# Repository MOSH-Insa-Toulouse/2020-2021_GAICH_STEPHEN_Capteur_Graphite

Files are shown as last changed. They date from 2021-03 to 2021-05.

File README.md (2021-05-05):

# 2020-2021 : Capteur Graphite GAICH-STEPHEN 
2020-2021 : Projet réalisé dans le cadre de l'Unité de Formation "du capteur au banc de test" en 4ème année Génie Physique, à l'INSA de Toulouse. Au cours de ce projet, nous avons réalisé un capteur de déformation/ jauge de contrainte à base de graphite 3H à 3B. Afin de mesurer la résistance de ce type de crayon, nous avons crée un dispositif bas-coût et transportable qui fut proposé par nos enseignants. Nous avons réalisé et fabriqué un PCB shield, à l'aide du logiciel Kicad, contenant un amplificateur transimpédance (circuit analogique) , un module Bluetooth, un écran OLED et un encodeur rotatoire. Ce dernier est pluggé sur un microcontrôleur Arduino Uno programmé à l'aide du logiciel Arduino IDE et contrôlé par une application android APK bluetooth. 

*** 
  - [Livrables](#livrables)
  - [PCB Shield](#pcb-shield)
  - [Code Arduino Mesure](#code-arduino-mesure)
  - [Application android APK](#application-android-apk)
  - [Banc de test](#banc-de-test)
  - [Code Arduino du banc de test](#code-arduino-du-banc-de-test)
  - [Protocole de test du capteur et les résultats obtenus](#protocole-de-test-du-capteur-et-les-résultats-obtenus)
  - [Datasheet capteur graphite](#datasheet-capteur-graphite)
  - [Problèmes rencontrés et améliorations à réaliser](#problèmes-rencontrés-et-améliorations-à-réaliser) 

*** 
## Livrables  

- [x] PCB shield 
- [x] Code Arduino permettant la mesure de R et le contrôle des fonctionnalités BT, OLED... 
- [x] Application android APK réalisé avec MIT APP INVENTOR.
- [x] Protocole de mesure et le programme Arduino pour le banc de test
- [x] Datasheet du capteur de déformation/ jauge de contrainte 

## PCB Shield
Utilisation des outils présents dans le logiciel Kicad pour créer le PCB: 
[KiCad EDA - Schematic Capture & PCB Design Software](https://kicad-pcb.org/), version: 5.1.8 

Le PCB Shield est pluggé sur un microcontrôleur Arduino Uno. Un amplificateur transimpédance, un module BT, un écran OLED et un encodeur rotatoire sont présents. 

Librairies de composants:
* Capacitor THT
* Resistor THT 
* Arduino Uno

#### Composants créés : symboles & empreintes 

- *Capteur Graphique*

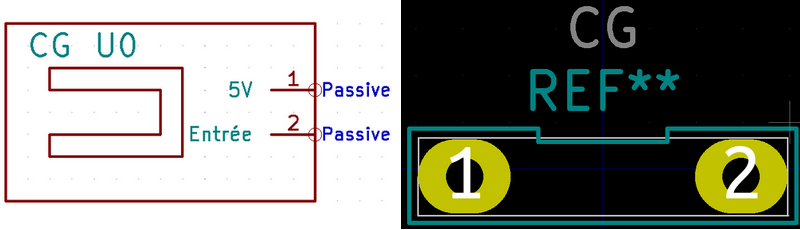
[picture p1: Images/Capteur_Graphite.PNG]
CG


- *Module Bluetooth*

BT

- *Encodeur rotatoire Keyes KY 040*

Encodeur

- *Ecran OLED*

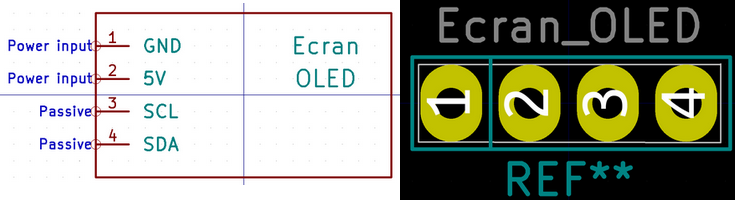
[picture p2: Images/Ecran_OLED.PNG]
Ecran


- *Amplificateur LT1050* (Empreinte déjà présente : DIP-8_W7.62mm_LongPads)

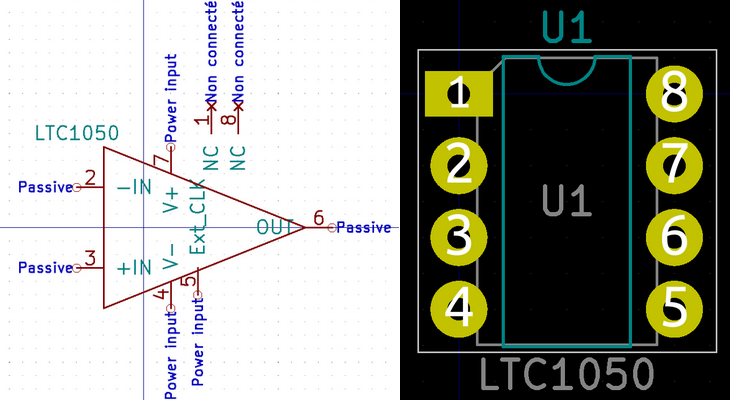
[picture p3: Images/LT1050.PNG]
LT1050


#### Schématique 

Dans le Eeschema, crée à partir d'un modèle Arduino Uno, nous avons regroupé les éléments suivant trois groupes : l'amplificateur transimpédance (circuit analogique qui permet de traiter les données envoyées par le capteur (variation de résistance)), les modules permettant d'ajouter des fonctionnalités au micro-contrôleur (module Bluetooth, encodeur rotatoire, écran OLED) et les broches de la carte Arduino Uno.  

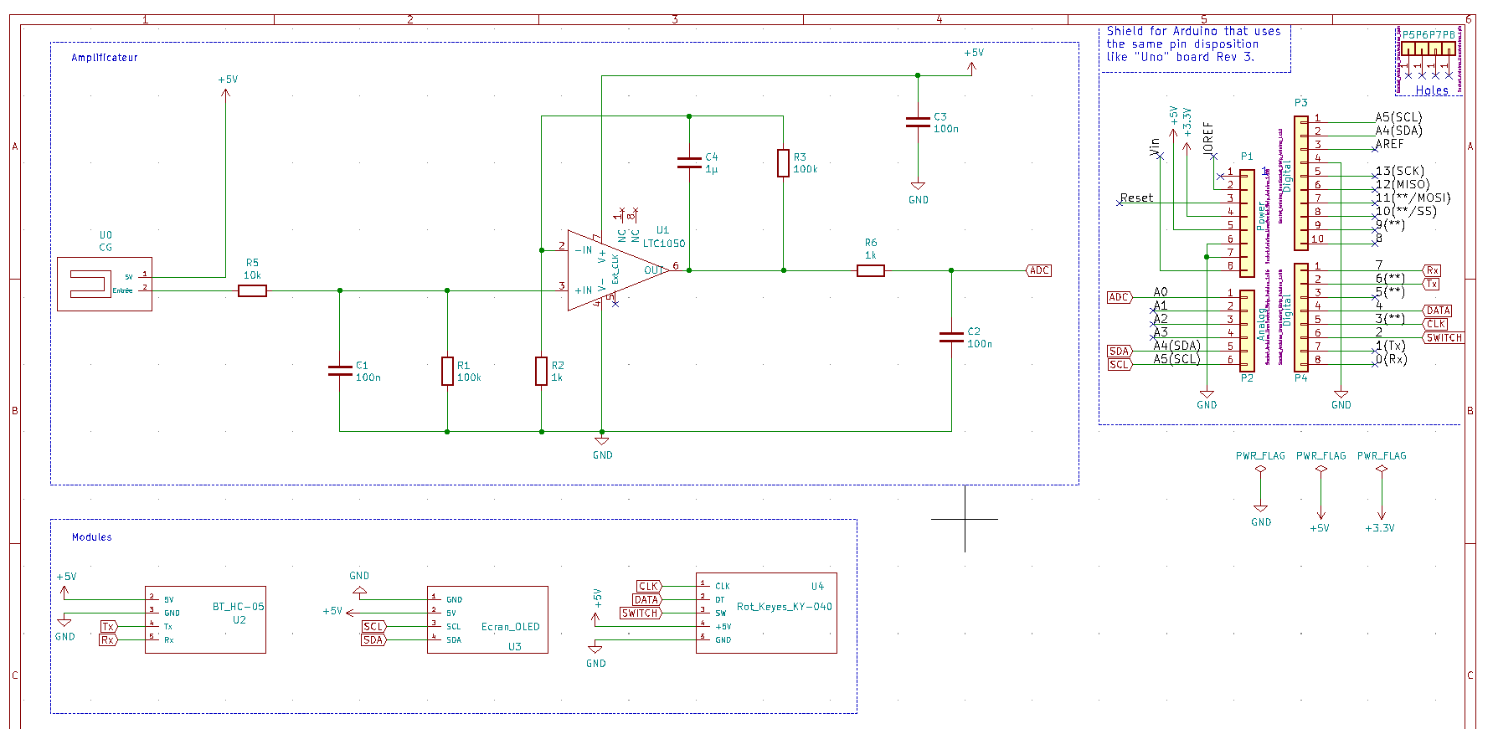
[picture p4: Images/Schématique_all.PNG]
Schematique


#### Placement des composants 

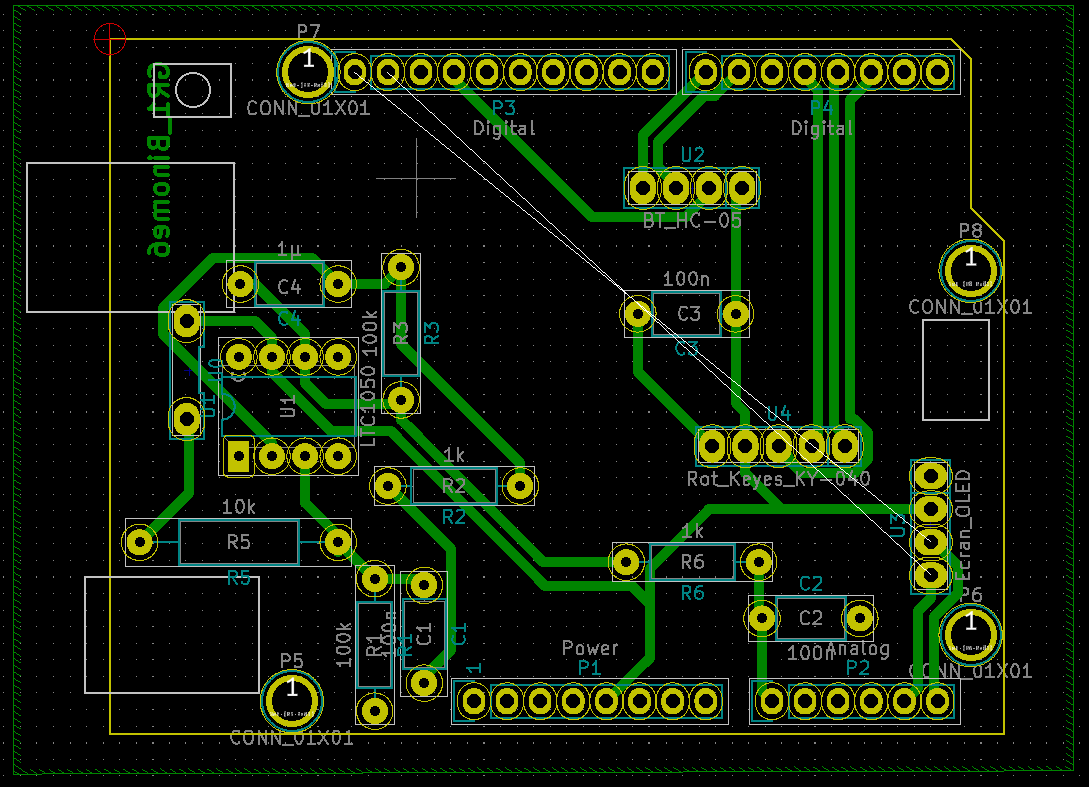
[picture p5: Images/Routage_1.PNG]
Placement


#### Routage 3D

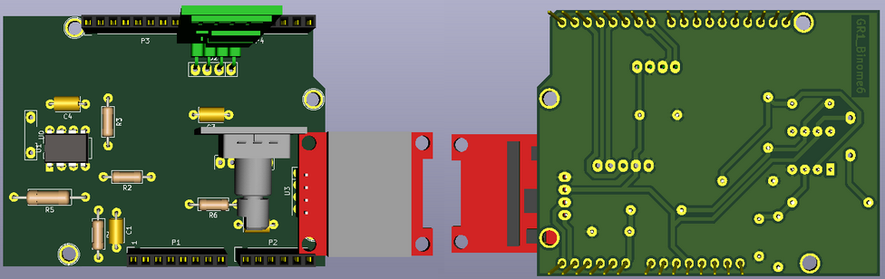
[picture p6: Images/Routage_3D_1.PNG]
Routage
 

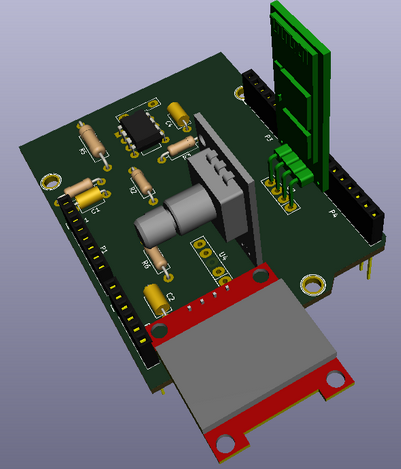
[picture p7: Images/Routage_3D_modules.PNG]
Routage


#### Soudage du PCB

Grâce à Catherine Crouzet, travaillant au Génie Physique, INSA Toulouse, nous avons pu réaliser notre PCB. Après avoir réalisé le schéma électrique, le placement des composants et le routage de la carte PCB sur le logiciel KiCad, le typon du PCB est imprimé sur deux feuilles calques. Les deux transparents sont alors superposés et scotchés entre eux afin de diminuer le risque de microcoupure (encre trop pale). Le typon est disposé sur la glace de l’insoleuse ainsi que la plaque d’époxy dont la face cuivrée (60µm) photosensible est "collée" au typon. Cette opération dure environ deux minutes et permet d’insoler la face photosensible. Le dessin du typon est alors visible sur la face cuivrée. La plaque est ensuite plongée dans un révélateur jusqu’à ce que le dessin apparaisse parfaitement (retire la résine non insolée). Après l’avoir rincé à l’eau, la plaque est alors prête pour la gravure. Le PCB est alors place dans un bain de perchlorure de fer rongeant tout le cuivre non protégé par la résine pendant sept minutes. Après l’avoir rincée à l’eau et vérifié le circuit, la résine est retirée avec de l’acétone. Le PCB sera ensuite percé et les composants seront soudés. 

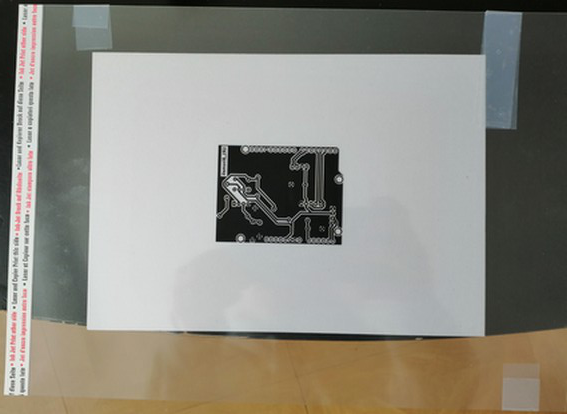
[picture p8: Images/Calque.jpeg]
Calque


Passons ensuite au perçage des trous de la plaquette à l'aide d'une perçeuse électrique [ici](Images/Perçeuse.jpg).
- 0.8mm pour ceux de l'AOP, des résistances et des capacités.
- 1mm pour ceux des connecteurs de l'Arduino et des headers des différents modules (pinces pour la feuille de graphite, bluetooth, encodeur rotatoire, écran OLED)

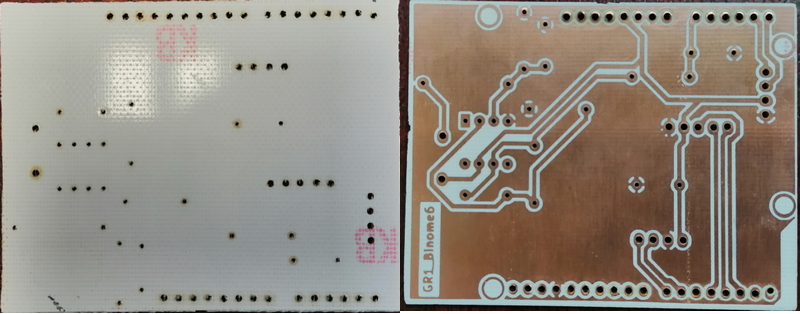
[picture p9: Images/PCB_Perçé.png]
Perçage


Pour finir, nous avons soudé chaque composant à l'aide d'un fer à souder. 

Remarque: il aurait fallu faire le diamètre des pads des connecteurs arduino plus gros afin d'avoir des soudures parfaites => peu de cuivre qui est resté autour après le perçage, ce qui a compliqué la soudure. 

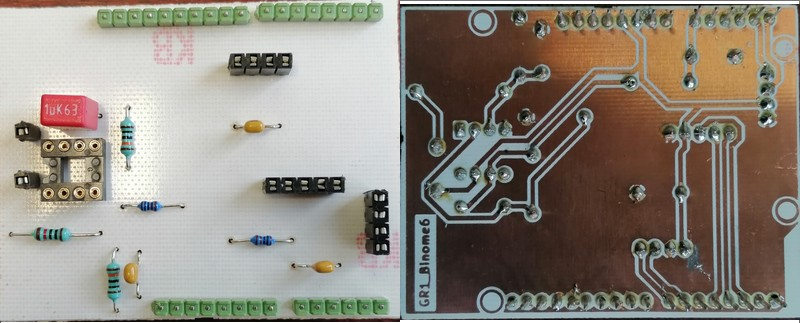
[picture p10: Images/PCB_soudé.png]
Soudure


#### Détail sur le conditionneur du capteur réalisé sur le shield (électronique analogique)
Nous avons détaillé cette partie dans la datasheet à la page 5 et 6 [ici](Datasheet/Datasheet_jauge_contrainte_GPINSA2021-2494-5215.pdf)

## Code Arduino Mesure 
Utilisation de l'environnement Arduino IDE téléchargeable [ici](https://www.arduino.cc/en/software); version 1.8.13.

Les librairies que nous avons utilisées sont disponibles [ici](PGM_Arduino_Mesure/Librairie).

Nous avons développé un programme permettant de mesurer la résistance de notre capteur. Vous pouvez le retrouver [ici](PGM_Arduino_Mesure/Programme_Capteur_Mesure/Programme_Capteur_Mesure.ino). 
Il s'agit d'un programme basique qui lira la valeur de la tension sur le pin A0 nommé comme "capteurgraphite". Cette acquisition est cadencée à 1s. La valeur lue est ensuite mappée sur 1 byte (0 à 255) car nous avons choisi d'envoyer un chiffre d'un byte sur le bluetooth. L'APK recevra un chiffre d'un byte à chaque tour de boucle. Cette valeur est également affichée sur le port série.

## Application android APK
Utilisation du site MIT App Inventor : [ici](https://appinventor.mit.edu/). 

Nous récupérons les données envoyées par le module bluetooth HC05 sur l'application et créons un fichier pour stocker ces dernières. 
Après de nombreux problèmes avec cet environnement et en s'inspirant du code crée par M.Grisolia, nous avons pu développer cette application. 

Face avant 

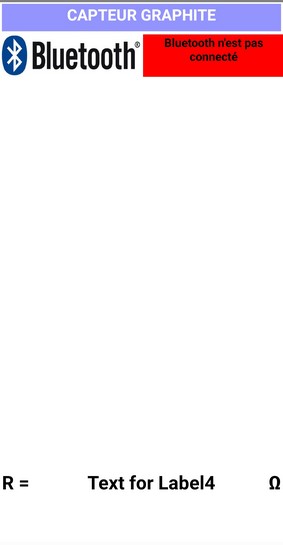
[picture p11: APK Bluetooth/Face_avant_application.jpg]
APKFaceAvant


Une connexion avec le bluetooth HC05 est nécessaire. Puis, vous pourrez suivre la variation de la tension lue par l'APK "en direct". La valeur de la résistance du capteur est aussi calculée et affichée en bas de l'écran. Enfin, un fichier contenant toutes les données récupérées par le bluetooth est créé dans vos documents. 

Vous trouverez le fichier .aia [ici](APK_Bluetooth/CAPTEUR_GRAPHITE_FILE.aia) et le fichier .apk [ici](APK_Bluetooth/CAPTEUR_GRAPHITE_FILE.apk)

Nous avons essayé d'améliorer cette version en faisant plusieurs screens. 
Une page d'accueil présente ci-dessous : 
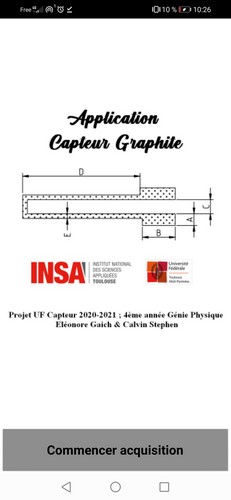
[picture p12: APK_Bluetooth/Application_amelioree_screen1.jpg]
page-accueil


Ensuite, sur la deuxième page après avoir cliqué sur le bouton "commencer l'acquisition", vous devez réaliser la mesure de la résistance initiale du capteur. Lorsque tous les voyants de l'étape 1 se mettent au vert, vous pouvez voir le tracé de la variation de la tension Vadc en fonction du temps au cours du temps. Les valeurs de la résistance du capteur et de la résistance relative sont aussi affichées.

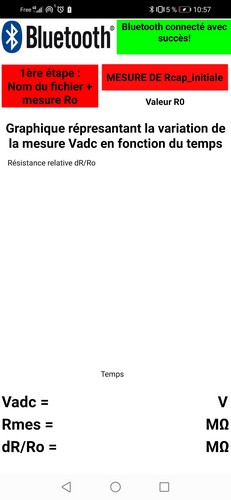
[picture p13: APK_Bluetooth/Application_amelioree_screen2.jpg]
Page-acquisition
 

Vous trouverez le fichier .aia [ici](APK_Bluetooth/Application_Capteur_amelioree.aia) et le fichier .apk [ici](APK_Bluetooth/Application_Capteur_amelioree.apk)

Plusieurs améliorations peuvent être réalisées. Nous les détaillerons dans la partie "Problèmes rencontrés et améliorations à réaliser".

## Banc de test 
Nous avons réalisé deux bancs de test "low-tech". Nous avons détaillé sa construction dans la datasheet afin que toute personne possédant notre capteur puisse retrouver les résultats que nous avons obtenus [ici](Datasheet/Datasheet_jauge_contrainte_GPINSA2021-2494-5215.pdf) à la page 7-8. De plus, étant réalisé à base de déchets ménagers, aucun matériel de haute technologie n'est nécessaire. 

Nous vous présentons nos deux bancs de test : 

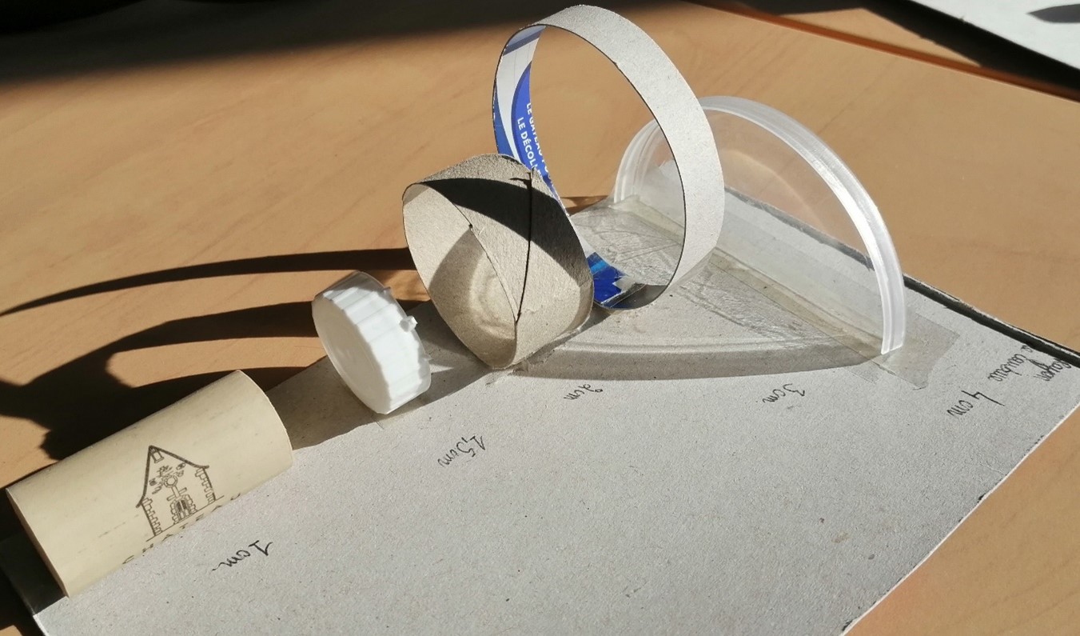
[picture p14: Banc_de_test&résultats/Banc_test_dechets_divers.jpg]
Banc_test_dechets


Figure : Banc de test « low-tech » n°1_ récupération de déchets divers

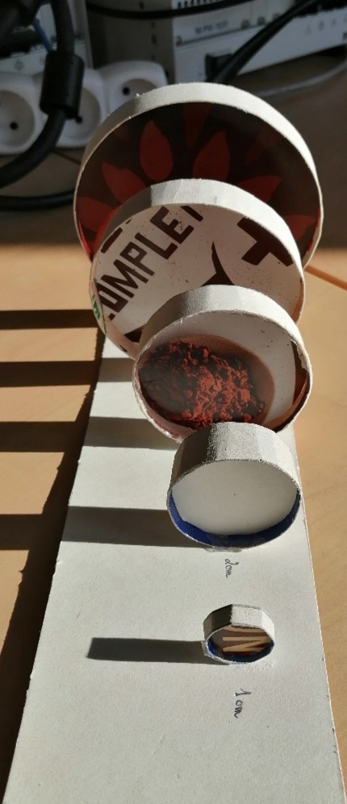
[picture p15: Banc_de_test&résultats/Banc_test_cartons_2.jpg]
Banc_test_carton


Figure : Banc de test « low-tech » n°2 _ carton

Au début, afin de diminuer les faux contacts entre les deux pinces crocodiles, nous avions utilisé un rouleau de papier toilette que nous avions troué (voir la photo ci-dessous).
Nous n'avons pas gardé cette méthode pour les mesures en tension et compression car les cercles créés sur le banc n'était pas à la même hauteur (amélioration possible).

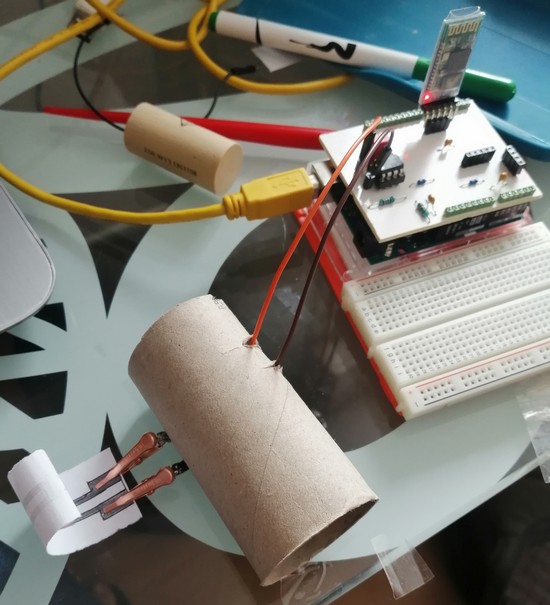
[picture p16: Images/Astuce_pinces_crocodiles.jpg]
Astucepince


## Code Arduino du banc de test 
Nous avons développé ce programme arduino afin de déterminer les valeurs obtenues en utilisant notre banc de test : [ici](PGM_Banc_de_test/PGM_Banc_de_test.ino).

Pour ce faire, nous avons du améliorer une librairie nous permettant de faire le "debouncing" sur l'encodeur rotatoire [ici](PGM_Arduino_Mesure/Librairie/Encoder_Polling_V2).

Notre nouveau programme gère aussi l'encodeur rotatoire et l'écran OLED. Ayant plusieurs banc de tests, nous avons programmé un menu sur l'écran OLED permettant à l'utilisateur de choisir le type de banc de test souhaité. Le boutton poussoir de l'encodeur rotatoire permet de selectionner ce dernier. Une fois le type de banc de test choisi, le programme envoie le type de banc de test à l'APK sous forme de "string" (texte). Dans le fichier des données enregistré sur le téléphone portable, chaque acquisition commence par des informations sur l'acquisition (banc de test, clock, forme des données reçues etc). Une fois cette étape terminée, l'OLED affiche la question "le bluetooth est- il connecté ?". L'utilisateur doit confirmer que la connexion a été établie en appuyant sur "Oui". Ensuite, il affiche "Etes-vous prêts ?" . L'utilisateur appuie de nouveau sur "Oui" une fois prêt. L'acquisition commence. La valeur de la tension Vadc est affichée sur l'OLED et est envoyée à l'APK via le bluetooth. Quand l'utilisateur souhaite arrêter l'acquistion, il doit appuyer sur le bouton 'STOP'. L'acquisition est alors arrêtée et l'OLED affiche de nouveau le menu principal.

## Protocole de test du capteur et les résultats obtenus 
Nous avons réalisé différentes expériences afin de déterminer les caractéristiques de notre capteur. 

#### Influence des dimensions du capteur 

Dans un premier temps, nous avons souhaité étudier l'influence des dimensions du capteur sur la résistance initiale. De ce fait, nous avons réalisé un plan d'expérience avec un modèle linéaire sans interactions de type TRI. Veuillez consulter ce document pour plus de détails sur la démarche : [ici](Banc_de_test&résultats/Banc_test_recherche_meilleur_capteur.docx) et sur les résultats obtenus [ici](Banc_de_test&résultats/Plan d'expérience_meilleures_dimensions.xlsx).

Nous avons pu identifier la réalité expérimentale (variables aléatoires de mesure) et tenter d’expliquer puis de maitriser au mieux les paramètres ayant un impact sur la résistance de notre capteur. Nous n’assurons pas que tous les paramètres influents furent identifiés. Elles ont aussi permis de vérifier que la résistance de notre capteur suivait la loi de Pouillet et donc la loi d’Ohm. Etant donné que nous ne sommes pas capables de déterminer le nombre de feuillets de graphite déposé lors du coloriage de notre capteur, nous allons étudier la variation relative en résistance ∆R/R_o = (R_mes-R_o)/R_o  afin d’homogénéiser nos mesures et pouvoir les comparer.  

#### Zone de non-déterioration du capteur

Dans un deuxième temps, nous nous avons essayé de determiner la zone de non-destruction du capteur. Après chaque mesure sur un rayon de courbure, nous avons noté la valeur de la tension du capteur au repos (non déformé) puis avons déterminé la résistance de ce dernier. Nous l’avons ensuite comparé à celle mesurée au début de la série de mesure. 
Document excel  [ici](Banc_de_test&résultats/Determination_zone_non_destruction_capteur.xlsx)

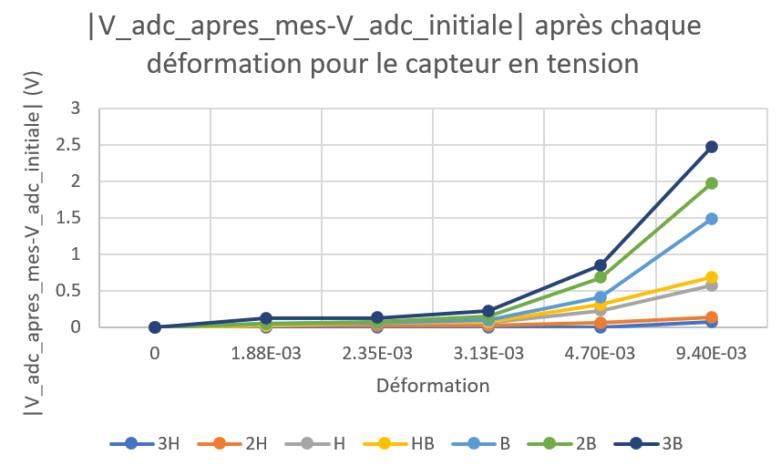
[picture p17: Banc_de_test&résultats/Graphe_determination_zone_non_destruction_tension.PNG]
Zone-non-destruction_tension


Figure : |Vadc_après_chaque_mesure - Vadc_initiale| après chaque déformation pour le capteur en tension

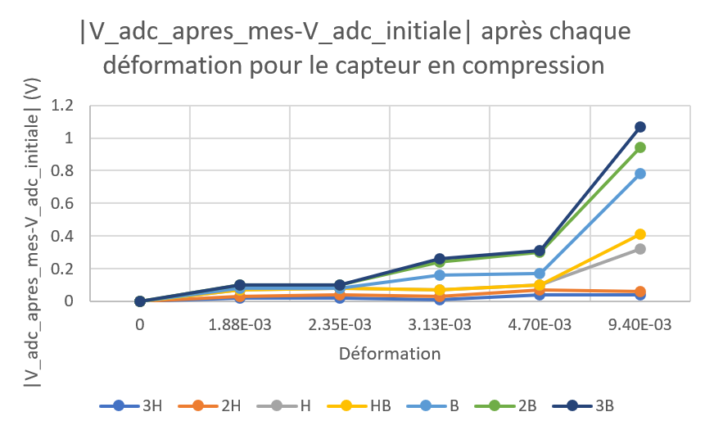
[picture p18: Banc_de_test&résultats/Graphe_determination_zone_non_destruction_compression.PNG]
Zone-non-destruction_tension


Figure : |Vadc_après_chaque_mesure - Vadc_initiale| après chaque déformation pour le capteur en compression

Voici notre conclusion : 

Zone-non-destruction

#### Influence du type de crayon utilisé pour colorier le capteur

Ensuite, nous avons étudie l'influence du type de crayon utilisé pour colorier notre capteur. Les crayons 3H, 2H, H, HB, B, 2B, et 3B furent testés successivement pour colorier notre capteur. Des tests de déformation, utilisant différents rayons de courbure de notre banc de test, sur ces capteurs furent réalisés. Ces informations sont présentes sur ces différents graphiques. Pour de détails, consultez le document excel [ici](Banc_de_test&résultats/Mesure_RayonCoubure_Crayons_Papiers.xlsx). 

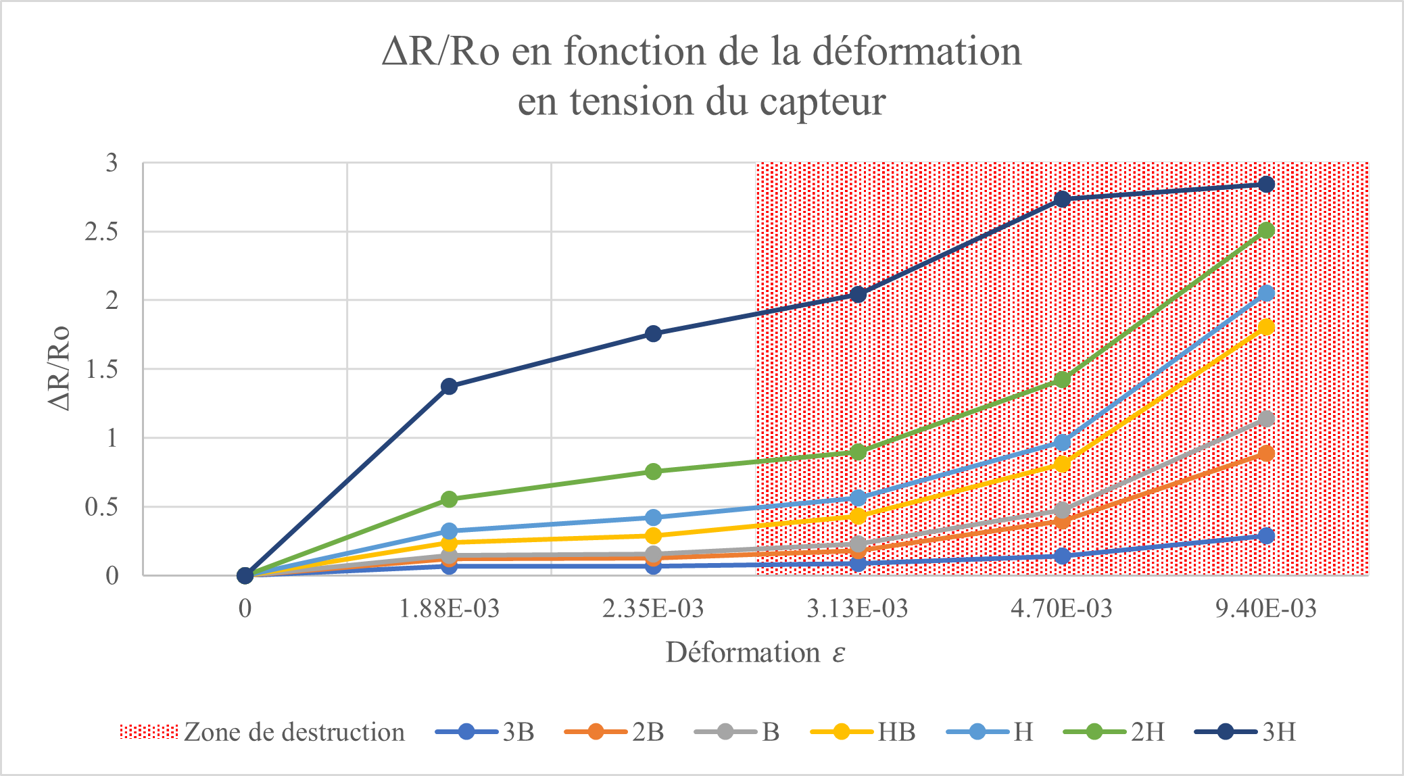
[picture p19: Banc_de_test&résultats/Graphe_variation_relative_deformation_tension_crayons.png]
Mesure_crayons_tension


Figure : Graphique représentant la variation relative de la résistance en fonction de la déformation en tension du capteur et du type de crayon présent sur le capteur

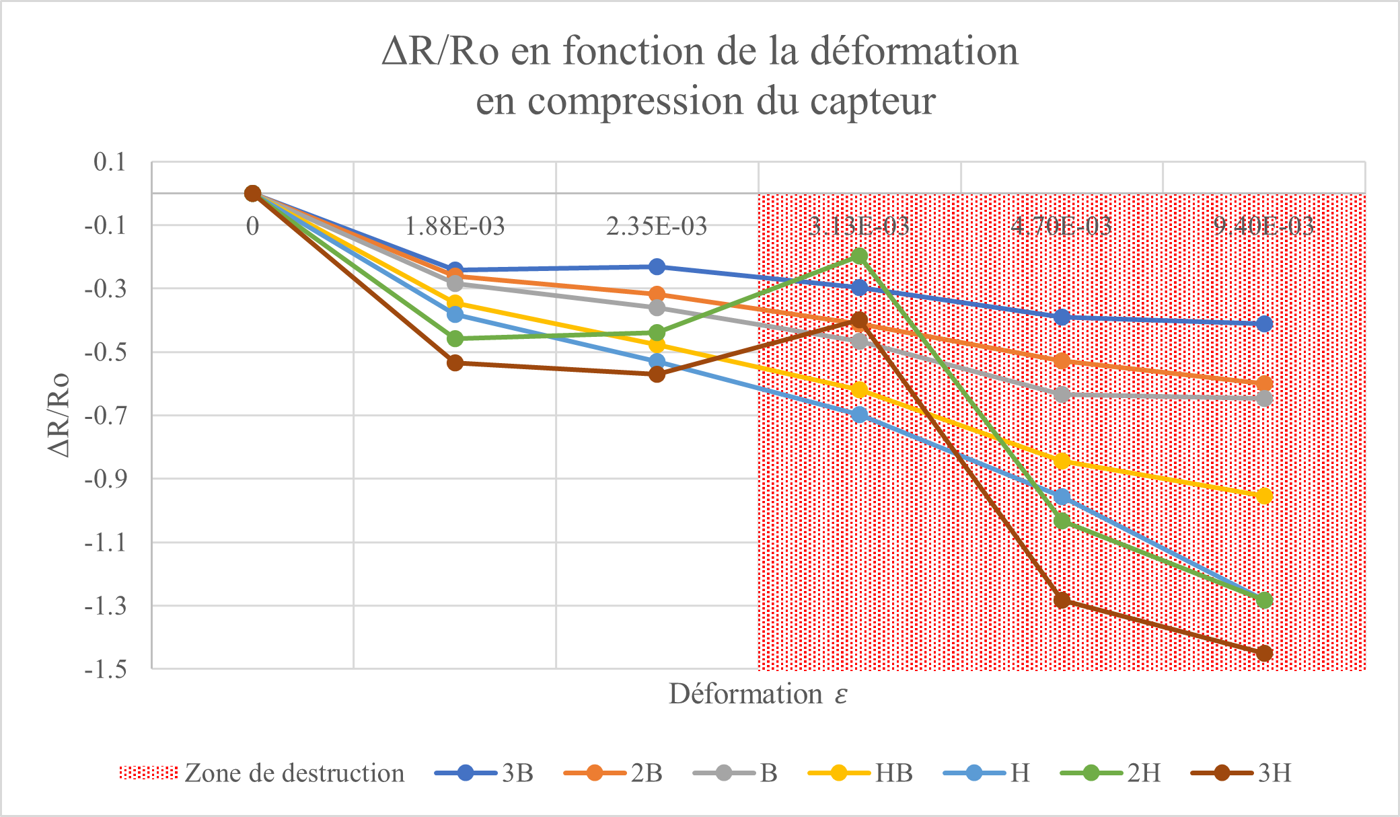
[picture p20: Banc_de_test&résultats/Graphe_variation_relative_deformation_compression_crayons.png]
Mesure_crayons_compression


Figure : Graphique représentant la variation relative de la résistance en fonction de la déformation en compression du capteur et du type de crayon présent sur le capteur

En conclusion de cette étude, le capteur colorié avec un crayon 3H est le plus sensible. En effet, pour ce capteur, la variation relative de la résistance ΔR/Ro est la plus grande. Cependant, en effectuant plusieurs expériences (colorier différents capteurs avec ce crayon), nous observons une large variabilité de la réponse. Lorsque le capteur est colorié avec des crayons 2H, H, HB, B, 2B et 3B, un comportement linéaire du ce dernier est observé. La sensibilité se définit comme le rapport entre sa valeur de sortie et sa valeur d'entrée. Lorsque le capteur est soumis à un mouvement de tension et de compression, la sensibilité du capteur augmente avec la dureté du crayon utilisé. En l’occurrence, le capteur colorié avec le crayon 3H est le plus sensible et celui colorié avec le crayon 3B est le moins sensible.

#### Influence du type de papier du capteur 

Enfin, nous avons étudié l'influence de type de papier. Nous avions émis l'hypothèse que la réponse du capteur serait différente en fonction du type de papier utilisé. Quand le capteur est réalisé sur du papier normal (70g/m²), la valeur de la résistance est trop faible pour être mesurée par notre conditionneur. La valeur de la tension Vadc est en saturation (5V). Une corrélation entre l’épaisseur du papier utilisé et la réponse du capteur existe. Nous avons détaillé une possible explication à ce phénomène dans la datasheet à la page 15. [ici](Datasheet/Datasheet_jauge_contrainte_GPINSA2021-2494-5215.pdf)

Pour pallier ce problème, le papier fut renforcé en enveloppant le capteur avec du ruban d’adhésif sans couvrir les pads du capteur pour la prise du contact avec les pinces crocodiles. Vous trouverez les résultats obtenus dans le fichier excel [ici](Banc_de_test&résultats/Influence_scotch.xlsx). En effectuant plusieurs tests sur le capteur, une tendance d'augmentation de la résistance est observée lorsque nous diminuons le rayon de courbure. Cependant, nous pouvons observer une augmentation initiale de la résistance entre un capteur scotché et un capteur sans ruban adhésif. Nous n’avons pas observé une amélioration de la zone de non-destruction. Dans certains cas, nous observons même une dégradation de cette dernière. Nous avons détaillé une possible explication à ce phénomène dans la datasheet à la page 15. [ici](Datasheet/Datasheet_jauge_contrainte_GPINSA2021-2494-5215.pdf)

## Datasheet capteur graphite
Vous pouvez retrouver la datasheet complète de notre capteur [ici](Datasheet/Datasheet_jauge_contrainte_GPINSA2021-2494-5215.pdf)

## Problèmes rencontrés et améliorations à réaliser

#### Problèmes sur le PCB

- Pads pour les connecteurs arduino trop fins.
- Mauvais placement de l'empreinte OLED : En testant l'écran OLED avec un programme fourni dans les libraires arduino, nous nous sommes rendus compte que, par inattention, nous avions mal placé l'empreinte (rotation 180°) car nous souhaitions que l'écran OLED soit positionné vers l'extérieur (cf PCB 3D). Afin d'avoir les bonnes pins, ce dernier doit être placé à l'intérieur. Or il y a l'encodeur rotatoire. Pour palier à ce problème, nous allons utiliser la platine d'expérimentation ou des fils males/femelle. 

  Améliorations : Nouveau PCB. 

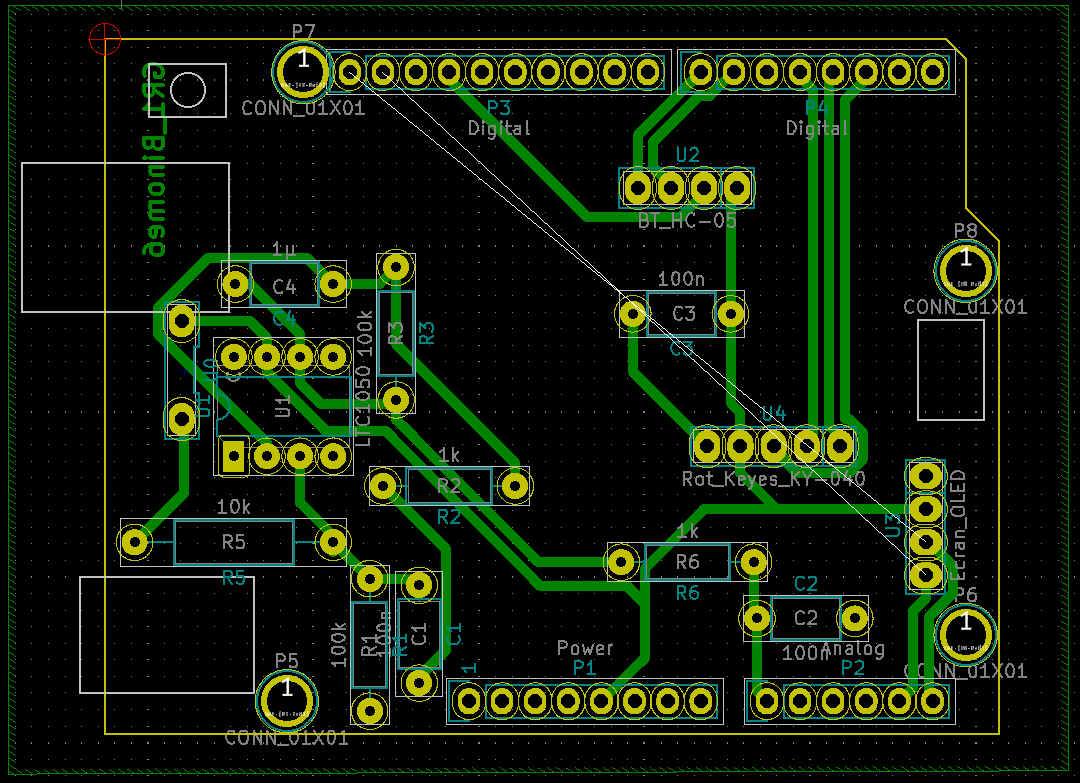
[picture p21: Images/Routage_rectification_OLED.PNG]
PCB_rectifié
  
  
#### Amélioration de l'application APK : Application capteur améliorée 
Après de multiples essais, nous n'avons pas réussi à afficher correctement la variation (dR-Ro)/Ro. Nous ne comprenons pas l'erreur commise. 
De plus, il faudrait optimiser le code pour que le traçage sur le canvas et les calculs de résistance se fassent en "temps réel". Nous avons un temps de décalage assez important. 
  
#### Améliorations sur la caractérisation du capteur 

Veuillez vous référer à notre datasheet présente [ici](Datasheet/Datasheet_jauge_contrainte_GPINSA2021-2494-5215.pdf) section Suggestions/Remarques. 

Nous avons détaillé différentes expérimentations que nous aurions aimées mener. Par manque de temps, nous n'avons pu les faire. 
De plus, afin de determiner concrètement les dimentions optimales du capteur, le plan d'expérience que nous avons mené devrait être complété par une étude plus approfondie (modèle de 2nd ordre) pour determiner l'optimum. Cependant, il faut pouvoir maitriser des paramètres qui ne sont pas contrôlables pour le moment (nombre de feuillets de graphite sur le capteur). 

***

## Note des auteurs 
Nous tenons à remercier Mme Crouzet, M.Grisolia et M.Biganzoli pour leur aide tout au long de ce projet ainsi que M.Constancias pour son aide lors de l'analyse des résultats obtenus sur notre DOE. 

Pour nous contacter : 
- Eléonore Gaich : gaich@etud.insa-toulouse.fr
- Calvin Stephen : stephen@etud.insa-toulouse.fr

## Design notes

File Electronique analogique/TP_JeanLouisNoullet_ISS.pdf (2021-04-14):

# ISS - UF Smart Devices : partie analogique

English version here

## 1. Mesure d'une résistance

Méthodes classiques :

- imposer I, mesurer V
- imposer V, mesurer I
- alimenter, mesurer V et I
- alimenter, mesurer R par identification (pont)

Cas du capteur de gaz à nano-particules :

- très faible courant : de l'ordre de 100 nA
- effet tunnel : forte non-linéarité de I(V)

Alors quelle technique adopter pour extraire l'information utile du capteur ?

## 2. Mesure de faible courant avec un micro-contrôleur

Parametres des microcontrôleurs courants en 2016
(AVR/Arduino, STM32, PIC Microchip, etc...) :
- résolution 10 à 12 bits (1024 à 4096 points)
- pleine échelle (VRef) de 1.1 V à 5.0 V
- impédance de source max 1 kOhm à 10 kOhm
- fréquence d'échantillonnage max 15 kHz à 2.4 MHz
La mesure directe d'un courant de 100 nA ne parait pas praticable.
N.B. la valeur max d'impédance de source est spécifiée en fonction de l' échantillonneur à capacité commutée présent à l'entrée de l'ADC.

Solution "classique" :

L'amplificateur transimpédance.

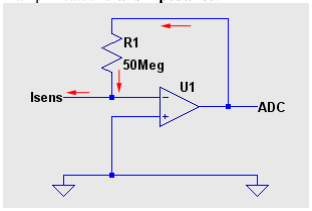
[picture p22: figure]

Problèmes posés par cette solution :

- nécessite une très grande valeur pour R1
- nécessite une tension négative pour alimenter le capteur

Solution "classique" améliorée :

L'amplificateur transimpédance suivi d'un étage amplificateur inverseur.

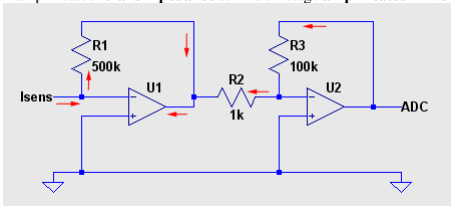
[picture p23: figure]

- grâce au gain du second étage, la résistance R1 n'a pas besoin d'être grande
- grâce à l'inversion, l'alimentation du capteur peut être positive
- cependant il faut une alimentation bipolaire pour les amplis

Solution minimaliste :

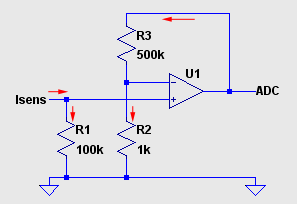
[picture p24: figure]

- conversion I-->U dans la résistance d'épreuve R1 (shunt)
- amplification à fort gain par montage non-inverseur
- la chute de tension sur R1 perturbe (un peu) la tension appliquée au capteur
- peut fonctionner avec seulement une alimentation positive

Remarques :
Gain de l’étage de l’AOP : (R2+R3)/R2=(1k+500k)/1k=501
Tension aux bornes de R1 : le courant Isens est d’environ 100nA
- V = 100kOhm*100nA=10⁻²V=10mV
Tension sur l’ADC : Gain*Tension aux bornes de R1 => 501*10x10⁻³~5V

Contraintes sur le choix de l'ampli :

- faible courant d'entrée

- ultra-faible offset de tension
- supporte mode commun à la tension d'alim négative ("low rail")

Remarques :
(1) offset voltage = erreur constante aux entrées de l’amplificateur différentiel dû à un état non compensé sur l’étage d’entrée de l’amplificateur. On veut que cet offset soit négligeable devant la tension mesurée sur R1 qui sera de 10mV.
(2) Le courant d’entrée doit être très petit devant Isens pour avoir le Isens traverse la R1 et pas l’entrée
(3) Mode commun : tension commune aux deux entrées, un bon amplifieur sera insensible à ce mode commun. Si le Isens =0A ,on veut 0V sur l’ADC. LTC1050C => 5µV offset voltage, et maximum offset voltage drift : 0.05µV/°C. Bien comparé aux 10mV aux bornes de R1.

L'ampli LTC1050C est disponible, satisfait-il ces contraintes ?

## 3. Filtrage passe-bas

Une bande passante de l'ordre de 1 Hz est largement suffisante pour extraire toute l'information utile du capteur, dont l'inertie est importante.

Un montage aussi sensible étant très vulnérable au bruit à 50Hz (+ harmoniques) résultant du couplage capacitif avec le réseau 230V, un filtrage passe-bas est indispensable.
D'autres sources de bruit à filtrer sont les horloges de circuits digitaux (microcontrôleur, afficheurs, etc...) et les transceivers RF (bluetooth, etc...).

Ce filtrage peut être effectué en partie du coté digital, par programme, sur le microcontrôleur.
Cependant un filtrage analogique est indispensable, en effet un excès de bruit à l'entrée de l'ADC pourrait amener celui-ci à saturation.
De plus un filtrage anti-repliement (anti-aliasing) est indispensable en raison de l'échantillonnage effectué par l'ADC.
Pour faciliter ce filtrage on a intérêt à faire fonctionner l'ADC à la plus GRANDE fréquence utilisable SANS PERTE DE QUALITE (dans le cas de l'Arduino Uno, 200kHz/13 = 15.4 kHz, avec un choix de prescaler à 128 ! (cf wiring.c).

Le filtrage peut s'implanter dans 3 régions de la chaîne de traitement analogique :

- filtre passif à l'entrée : permet d'éviter que les bruits HF causent de la distorsion dans les étages d'entrée
- filtre actif basé sur les amplificateurs opérationnels : maximum d'efficacité
- filtre passif en fin de chaine, coté ADC, pour retirer le bruit introduit en cours de traitement (bruit d'alimentation, bruit d'horloge des amplificateurs à découpage)

Schéma Suggéré

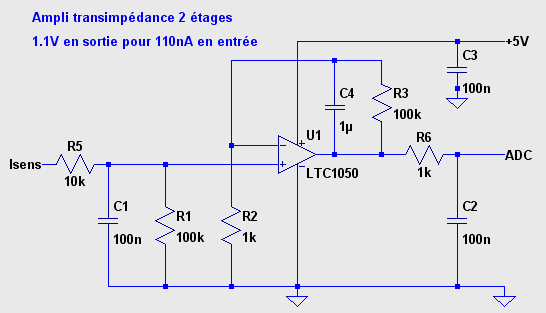
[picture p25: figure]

- R5 en entrée protège l'ampli opérationnel contre les décharges électrostatiques, en forme avec C1 un filtre pour les bruits en tension
- C1 avec R1 forme un filtre pour le bruit en courant
- R2 sera interchangeable, pour permettre une adaptation du calibre
- C4 avec R3 forme un filtre actif
- C2 avec R6 forme le filtre de sortie
- C3 filtre le bruit d'alimentation

## 4. Questions

A l’aide du simulateur LTSpice IV :

1. Vérifier la fonctionnalité dans les conditions nominales 2. L'incidence de l'offset de l'amplificateur LTC1050C est-elle acceptable ? 3. L'incidence du courant d'entrée de l'amplificateur est-elle acceptable ? 4. Quelle est la fréquence de coupure de chaque étage de filtre passe-bas ? 5. Quelle est l'atténuation globale d'un bruit en courant de 50 Hz ?

6. Quelle est l'atténuation globale d'un bruit en courant à la fréquence limite de repliement (dans le cas de l'ADC Arduino Uno) ?

### 7. Préparez une simulation de démonstration avec :

- un capteur alimenté en 5V dont la conductance varie de 10 nS à 20 nS en 0.5s (l’utilisation d’un filtre passe-bas pourrait être utile !).

### 1. Mettre en évidence l’intérêt du filtrage 50Hz choisi en visualisant

l’impact d’un bruit de 1% sur la source d’alimentation du capteur

### 2. Quand est-ce que ce bruit devient gênant ?

- Pour s’approcher des conditions réelles de mesures réalisées à l’AIME, vous modifierez le montage précédent pour mettre une alimentation de 20V sur le capteur (à la place de la 5V) et conserverez l’alimentation de 5V sur l’AOP.

### 1. Peut-on réaliser ce montage sur un Arduino Uno ?

- une source de bruit de 230V RMS à 50Hz, couplée au noeud d'entrée par une capacité de 1 pF
- Serait-il intéressant d’ajouter un montage dérivateur pour mesurer directement le coefficient cinétique de la réaction chimique du capteur avec un gaz ?

### 1. Si oui, proposez un montage !

N.B. pour simuler une conductance variable, utiliser l'élément Arbitrary current source (symbole BI) de LTSpice contrôlé par une source de tension indépendante représentant la variation de concentration du gaz atteignant le capteur

8. Donner une expression analytique de la résistance du capteur en fonction des éléments du circuit transimpédance.

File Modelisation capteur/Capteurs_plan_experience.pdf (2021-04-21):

Imprimé avec une version d'essai de
QCAD Professional

Merci d'essayer QCAD/CAM. Cette version d'essai vous permet d'essayer QCAD/CAM avant de

décider si vous voulez l'acheter. Il n'est pas destiné à un usage productif. Pour commencer à utiliser QCAD/CAM de façon productive, S'il

vous plaît achetez une version complète pour un prix modique auprès de notre boutique en ligne: qcad.org/shop. Avec votre achat, vous soutenez le développement futur de

QCAD. Merci!

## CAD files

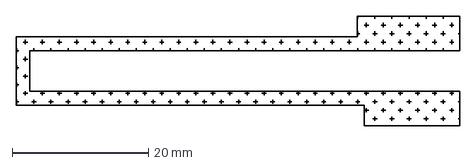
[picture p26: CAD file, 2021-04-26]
Modelisation capteur/Modelisation_capteur.dxf
65.0 x 16.0 mm

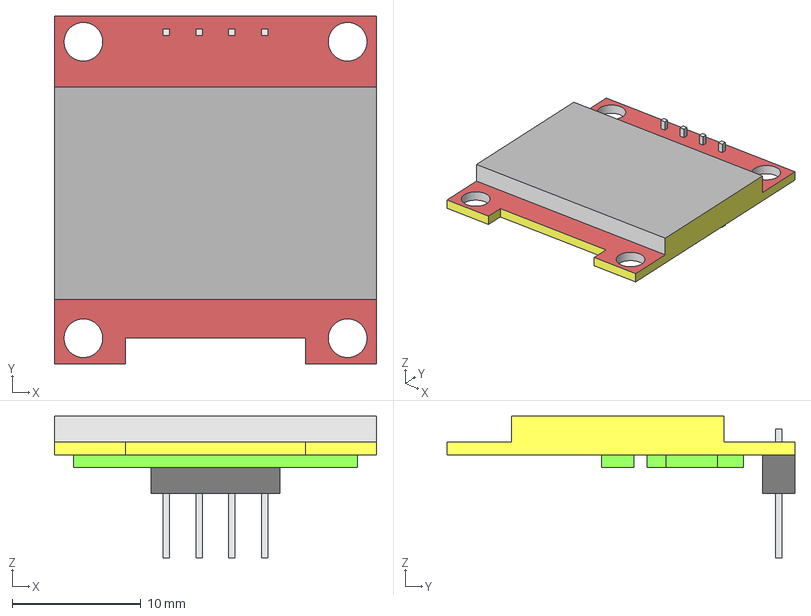
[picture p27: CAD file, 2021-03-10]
PCB_Shield/OLED_i2c_screen_3D.step
25.0 x 27.0 x 11.0 mm

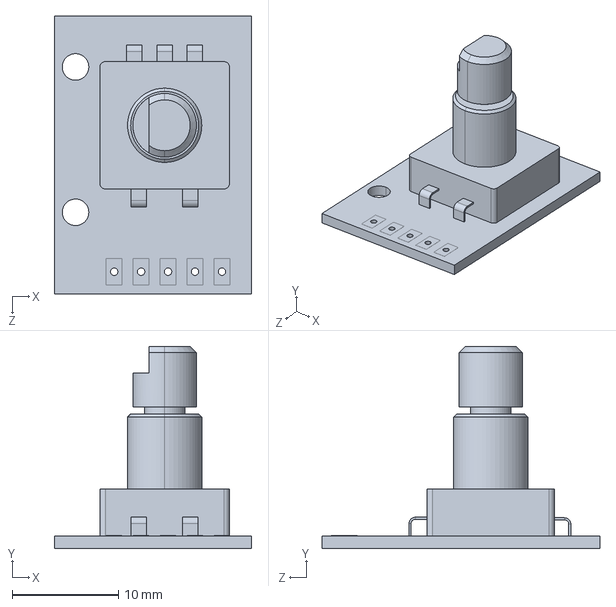
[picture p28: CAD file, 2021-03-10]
PCB_Shield/rotary-encoder-ky-040-1_3D/Encoder KY-040.STEP
18.6 x 19.1 x 26.2 mm

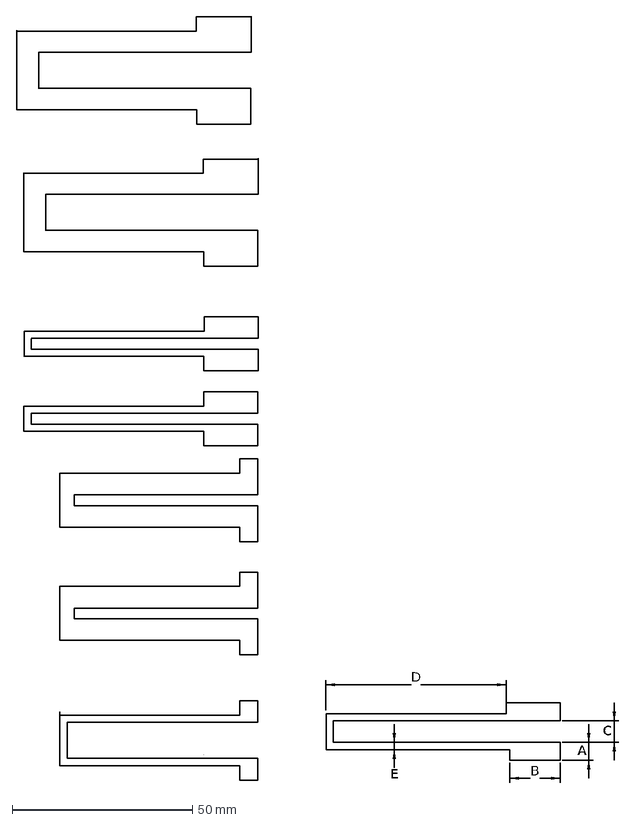
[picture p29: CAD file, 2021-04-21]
Modelisation capteur/#Capteurs_plan_experience.dxf
D
C
A
B
E

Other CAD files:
Modelisation capteur/Capteurs_plan_experience.dxf
PCB_Shield/rotary-encoder-ky-040-1_3D/Encoder KY-040.SLDPRT

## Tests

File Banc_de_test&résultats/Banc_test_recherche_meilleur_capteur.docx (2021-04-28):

RECHERCHE DU MEILLEUR CAPTEUR GRAPHITE

Déformation du capteur => coef de Poisson : déformation latérale et déformation longitudinale => comment le déterminer ? On néglige la déformation latérale ?

1ère étape : déterminer les dimensions idéales du capteur

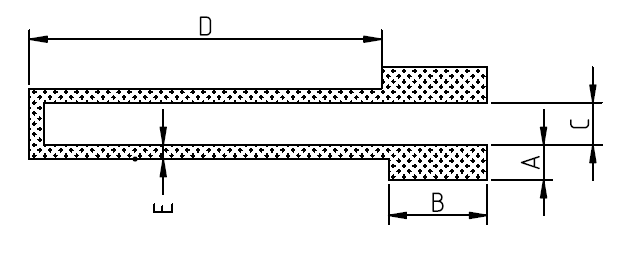
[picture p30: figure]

Légende :

A : largeur des pads [0.5 ; 1]cm

B : hauteur du pad [0.5 ; 1.5]cm

C : écartement des pads [0.3 ; 0.6]cm

D : longueur du capteur [1 ;5]cm

E : largeur du capteur [0.2 ;0.6]cm

Paramètre qu’on ne peut pas prendre en compte : nombre de feuilles de graphite déposé sur la feuille papier + le nombre de fibres papier qui sont rompus lors d’un essai

Détail plan d’expérience fichier excel

Faire un plan d’expérience avec modèle linéaire en prenant matrice Hadamard avec -1 : valeur min testée et 1 : valeur max en faisant une matrice normalisée

Chaque capteur sera testé sur un rayon de courbure du banc de test « low tech » :

- 1cm
- 2cm
- 3cm
- 4cm
- 5cm

Bilan :

1. Biais de mesure, id des paramètres expérimentaux que nous ne maitrisons pas => nombre de feuille de graphite déposé, coloriage régulier => INFLUENCE grandement la mesure (vu aussi avec les crayons graphite). Grande variabilité des résultats.
2. Vadc = 0 : pourquoi ? Seulement par le peu de graphite déposé ? Résultat d’une mesure en dehors de la sensibilité de l’ampli/ chaine d’instrumentation => Faire un étalonnage de la sensibilité de la mesure avec des résistances étalons et vérifier la précision (suggestions). Voir si certaines électrodes => pinces croco prennent de bonnes prises de contact pour quelque chose d’aussi faibles ? Un autre moyen de prendre le contact qui serait plus fiable et précis ? Ex : fourmi sur pèse personne => poids ?
3. Procédé de fabrication est très variable => propriétés du matériau déposées sont aussi variables. Feuillets de graphite déposés par coloriage => changement de la résistivité + points de contact qui influencent la résistance totale du capteur.
4. Comment s’assurer de la répétabilité de nos expériences : se fixer des conditions sur le coloriage ? Force, sens ? Conditions sur les prises de contact ? Où, comment ? => changement visible en fonction de l’endroit sur le pad différent : du au nombre de feuillets de graphite déposé mais aussi à un autre paramètre ? Pinces croco ayant une R trop importante ?
5. Définition de la résistance : résistivité qui dépend de la longueur + section de la conduction => ici vérifier avec les paramètres C,D,E + nombre de couches de graphite (vu au niveau des valeurs de R mesurées mais pas possible de le déterminer) => comment estimer l’epaisseur d’un trait de graphite => permettrait de remonter au nombre de feuillets de graphite déposées à l’origine de la conductivité : avec une balance de précision ? Assez précis ? http://wiki.scienceamusante.net/index.php/Estimer_l%27%C3%A9paisseur_d%27un_trait_de_crayon_%C3%A0_papier

Avec un profilomètre comme en TP AIME ? Avec une jauge d’épaisseur => problème avec le papier ?

Possible avec l’ellipsométrie est une méthode de caractérisation optique, basée sur l’analyse de l’état de polarisation (souvent elliptique) d’une lumière initialement polarisée après sa réflexion sur une surface ? Etant donné qu’il y aurait aussi deux surfaces : papier et graphite?

Bilan des expériences : Identifier la réalité expérimentale qui apporte des variables aléatoires de mesures => tente de maitriser au mieux : d’autres paramètres entrent en jeu ? + montrer que la résistance du capteur de graphite est fonction de la longueur et section du capteur => donc comportement représentatif de la déf de la résistivité.

2ème étape : influence du type de papier sur le capteur

Refaire les tests avec le capteur ayant les dimensions idéales pour notre banc de test avec :

- Papier normal
- Papier canson
- Papier donné par M. Grisolia (épaisseur ?)
- Avec scotch

Bilan : Papier normal => overload si on colorie de la même manière que sur le papier de Grisolia.

Influence de l’épaisseur du papier sur la mesure : pourquoi ? Les fibres du papier seraient-elles un frein sur la propagation du courant dans les feuillets de graphite ? Lorsqu’elles se rompent, nous remarquons que le capteur ne mesure absolument pas les mêmes valeurs => zone de détérioration. Comment réussir à renforcer ces fibres ? Mettre du scotch sur tout le capteur pas une bonne idée car diminution de la résistance initiale du capteur + pas d’amélioration de la zone de détérioration voire pire.

Le ruban adhésif est composé d’un film support transparent ou coloré et d’une colle qui permet l’adhérence de celui-ci sur tous types de surfaces.

### · Le film support

Il est soit en PVC soit en polypropylène (PP). La différence de matière influe sur le sens du déroulement et le bruit que le ruban produit durant ce déroulement. Ainsi, un ruban adhésif en PVC s’étire en travers tandis qu’un ruban adhésif PP s’étire dans le sens classique du déroulement. Le ruban adhésif PP est généralement bruyant lors du déroulement (certains modèles ont été conçus pour être silencieux) tandis que le ruban adhésif PVC n’émet aucun son. Plus le film support est épais, plus il résistera facilement à la déchirure et au cisaillement. Cela est notamment pratique lors de la pose d’un ruban adhésif sur les angles d’une caisse carton.

Le film support peut être de différentes couleurs : il peut être de couleur Havane (marron clair) mais il est souvent sans couleur c’est-à-dire transparent. Maintenant, il existe toute une gamme de couleurs : bleu, rouge, vert, jaune, orange, etc.

### · La colle

Il existe trois types de colles différents permettant une adhérence plus ou moins forte du ruban adhésif sur une surface : la colle solvant, la colle acrylique et la colle Hot Melt.

La colle solvant est à base de caoutchouc naturelle dissous dans un solvant. Son pouvoir d’adhésion est instantané y compris sur les matières plastiques. Elle résiste au froid et est recommandée pour les longs stockages. La colle acrylique résiste parfaitement aux UV mais pas au froid. La colle Hot Melt est fabriquée à base d’eau. Elle résiste aux grandes fluctuations de températures et à l’humidité. Grâce à une légère pression lors de la pose, vous pouvez améliorer l’adhérence de ce ruban adhésif.

http://www.adhesif1euro.com/de-quoi-est-compose-un-ruban-adhesif/

Peut-être en mettre que du coté où pas de graphite ?

Comment renforcer des fibres de papier ? Prendre quelque chose de plus épais ? Scotch spécial permettant tout de même la conduction du courant dans les feuillets de graphite ? Réellement low tech ?

3ème étape : influence du crayon sur le capteur

Tests avec des crayons HB, B, 2B, 2H

Pour le moment => donne l’impression que la mesure de la R dépend surtout de comment on colorie car colorier avec du 3H => résistance très faible si on le fait de la même manière que le HB donc comment déterminer réellement l’influence du type de crayon ?

4ème étape : trouver les zones de détérioration du capteur en fonction du rayon de courbure

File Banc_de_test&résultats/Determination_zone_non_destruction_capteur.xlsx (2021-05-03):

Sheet: Tension_HB
Determination de la zone de non-destruction en tension du capteur (crayon : HB)
 |  |  |  |  |  |  |  | Paramètres pour calcul de Rcapteur
 |  |  |  |  |  |  |  | R1 | 100000.0 | Vcc | 5
 |  |  |  |  |  |  |  | R2 | 1000.0 | R5 | 10000
 |  |  |  |  |  |  |  | R3 | 100000
 |  |  |  |  |  |  |  | Dimensions du capteur (mm) |  | A | 0.45 | B | 1.05 | C | 0.3
 |  |  |  |  |  |  |  |  |  | D | 2.35 | E | 0.2
 |  |  |  |  |  |  |  | Type de feuille (grammage) |  |  | 160g/m²
 |  |  |  |  |  |  |  | Expérimentateur coloriage |  |  | Calvin
 |  |  | Rayon de courbure (cm) |  |  |  |  |  |  |  | Rayon de courbure (cm)
Mesure n° |  | Sans rayon | 5 | 4 | 3 | 2 | 1 |  |  | Ro_initiale | 5 | 4 | 3 | 2 | 1
1 | Valeur de Vadc | 0.3 | 0.35 | 0.32 | 0.25 | 0.23 | 0.15 |  | Ro_apres_mesure | 168223333.3 | 168223333.3 | 168223333.3 | 168223333.3 | 210306666.7 | 280445555.6
 | Vadc après mesure sans rayon |  | 0.3 | 0.3 | 0.3 | 0.24 | 0.18 |  | |Ro_apres_mes - Ro_initiale| | 0 | 0 | 0 | 0 | 42083333.33 | 112222222.2
 | |Vadc_apres_mes - Vadc_initiale| | 0 | 0 | 0 | 0 | 0.06 | 0.12
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

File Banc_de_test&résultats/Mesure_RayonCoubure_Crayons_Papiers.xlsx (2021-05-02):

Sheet: Mesure_3H
Mesure de la résistance relative avec le crayon 3H
 | Paramètres pour calcul de Rcapteur
 | R1 | 100000.0 | Vcc | 5
 | R2 | 1000.0 | R5 | 10000
 | R3 | 100000
 | Dimensions du capteur (mm) |  | A | 0.45 | B | 1.05 | C | 0.3
 |  |  | D | 2.35 | E | 0.2
 | Type de feuille (grammage) |  |  | 160g/m²
 | Expérimentateur coloriage |  |  | Calvin
MESURE EN TENSION
 |  |  | Rayon de courbure (cm) |  |  |  |  |  |  |  | Rayon de courbure (cm)
Mesure n° |  | Sans rayon | 5 | 4 | 3 | 2 | 1 |  |  | Ro | 5 | 4 | 3 | 2 | 1
1 | Valeur de Vadc | 0.6 | 0.33 | 0.3 | 0.28 | 0.26 | 0.45 |  | Rcap | 84056666.67 | 152920303 | 168223333.3 | 180247142.9 | 194120769.2 | 112112222.2
 | Vadc après mesure sans rayon |  | 0.6 | 0.6 | 0.6 | 0.6 | 0.52 |  | ΔR/Ro | 0 | 0.8192525245 | 1.001308641 | 1.144352733 | 1.309403607 | 0.333769547
2 | Valeur de Vadc | 0.2 | 0.16 | 0.14 | 0.13 | 0.1 | 0.14 |  | Rcap | 252390000 | 315515000 | 360604285.7 | 388351538.5 | 504890000 | 360604285.7
 | Vadc après mesure sans rayon |  | 0.2 | 0.15 | 0.13 | 0.13 | 0.15 |  | ΔR/Ro | 0 | 0.2501089584 | 0.4287582143 | 0.538696218 | 1.000435833 | 0.4287582143
MESURE EN COMPRESSION
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

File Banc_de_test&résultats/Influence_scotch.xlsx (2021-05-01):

Influence du scotch sur la mesure (crayon : HB)
 | Paramètres pour calcul de Rcapteur
 | R1 | 100000.0 | Vcc | 5
 | R2 | 1000.0 | R5 | 10000
 | R3 | 100000
 | Dimensions du capteur (mm) |  | A | 0.45 | B | 1.05 | C | 0.3
 |  |  | D | 2.35 | E | 0.2
 | Type de feuille (grammage) |  |  | 160g/m²
 | Expérimentateur coloriage |  |  | Calvin
 |  |  | Rayon de courbure (cm) |  |  |  |  |  |  |  | Rayon de courbure (cm)
Mesure n° |  | Sans rayon | 5 | 4 | 3 | 2 | 1 |  |  | Ro | 5 | 4 | 3 | 2 | 1
1 (avec scotch) _ tension | Valeur de Vadc | 1.08 | 1.01 | 0.96 | 0.89 | 0.91 | 0.73 |  | Rcap | 46649259.26 | 49890000 | 52494166.67 | 56631573.03 | 55384505.49 | 69068082.19 | Vadc sans scotch initiale | 1.9
 | Vadc après mesure sans rayon |  | 0.99 | 0.98 | 0.98 | 0.95 | 0.73 |  | ΔR/Ro | 0 | 0.06947035799 | 0.1252947528 | 0.2139865441 | 0.1872536965 | 0.4805826135
2 (avec scotch) _ tension | Valeur de Vadc | 1.6 | 1.5 | 1.48 | 1.46 | 1.4 | 1.18 |  | Rcap | 31452500 | 33556666.67 | 34011621.62 | 34479041.1 | 35961428.57 | 42686610.17 | Vadc sans scotch initiale | 1.84
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

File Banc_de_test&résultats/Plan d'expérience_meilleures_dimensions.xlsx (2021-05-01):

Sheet: Tri
Capteur graphite : meilleures dimensions
 |  |  |  |  |  |  |  |  |  |  |  |  |  | Matrice de Hadamard H8 => car 5 paramètres à prendre en compte
 |  |  |  |  |  |  |  | Paramètres pas pris en compte |  |  |  |  |  | 1 | 1 | 1 | 1 | 1 | 1 | 1 | 1
 |  |  |  |  |  |  |  | * Le nombre de couche de graphite mis => pas mesurable |  |  |  |  |  | 1 | -1 | 1 | -1 | 1 | -1 | 1 | -1
 |  |  |  |  |  |  |  | * Le nombre de fibres papier qui sont rompus lors d’un essai |  |  |  |  |  | 1 | 1 | -1 | -1 | 1 | 1 | -1 | -1
 |  |  |  |  |  |  |  | Legende |  | A : largeur des pads [0.6 ; 1]cm |  |  |  | 1 | -1 | -1 | 1 | 1 | -1 | -1 | 1
 |  |  |  |  |  |  |  |  |  | B : hauteur du pad [0.5 ; 1.5]cm |  |  |  | 1 | 1 | 1 | 1 | -1 | -1 | -1 | -1
 |  |  |  |  |  |  |  |  |  | C : écartement des pads [0.3 ; 1] cm |  |  |  | 1 | -1 | 1 | -1 | -1 | 1 | -1 | 1
 |  |  |  |  |  |  |  |  |  | D : longueur du capteur [1 ;5]cm |  |  |  | 1 | 1 | -1 | -1 | -1 | -1 | 1 | 1
 |  |  |  |  |  |  |  |  |  | E : largeur du capteur [0.2 ;0.6]cm |  |  |  | 1 | -1 | -1 | 1 | -1 | 1 | 1 | -1
 |  |  |  |  |  |  |  |  |  |  |  |  |  | Générer des nombres aléatoires entre bornes : = min + alea()*(max-min)
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

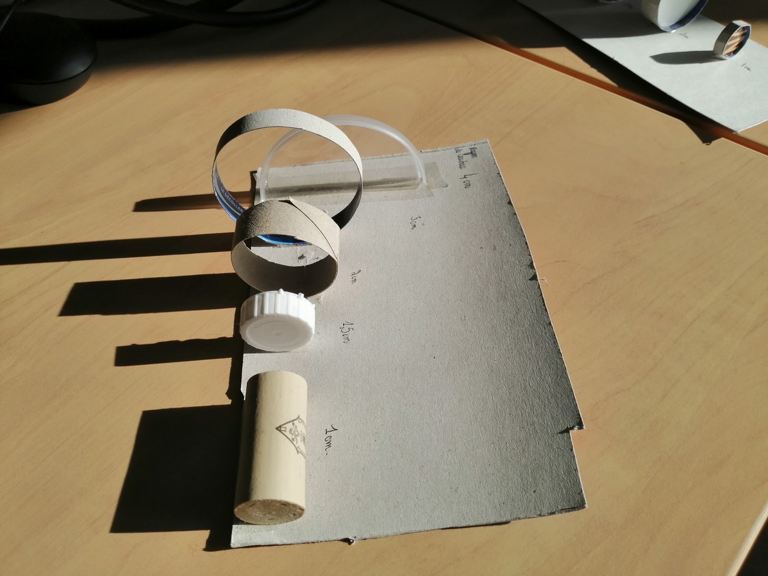
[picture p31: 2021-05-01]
Banc_de_test&résultats/Banc_test_dechets_divers_2.jpg

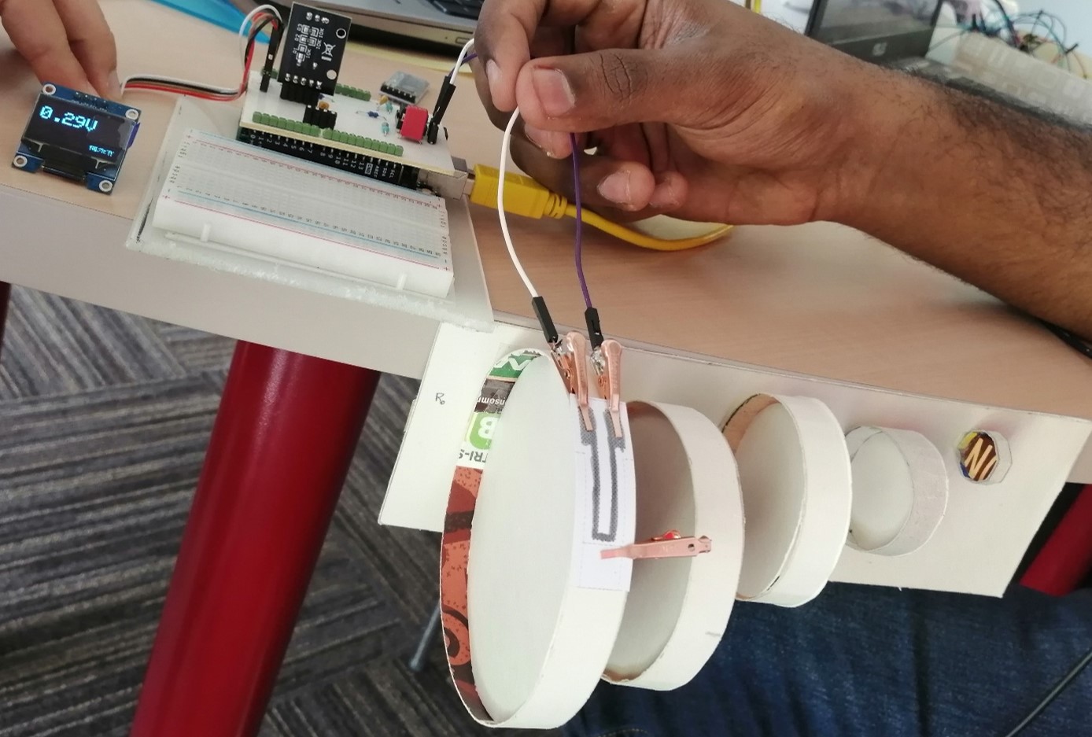
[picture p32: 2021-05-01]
Banc_de_test&résultats/Mesure en tension.jpg

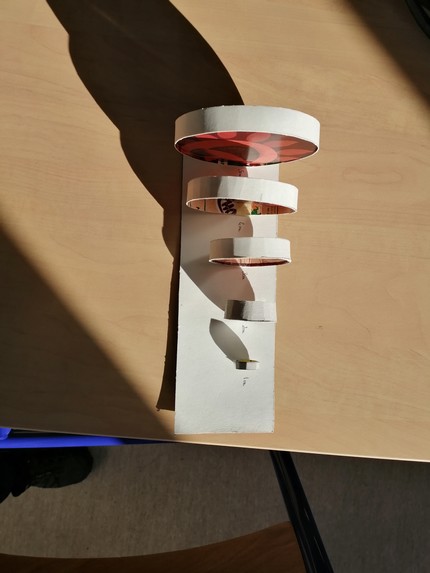
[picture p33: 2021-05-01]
Banc_de_test&résultats/Banc_test_cartons.jpg

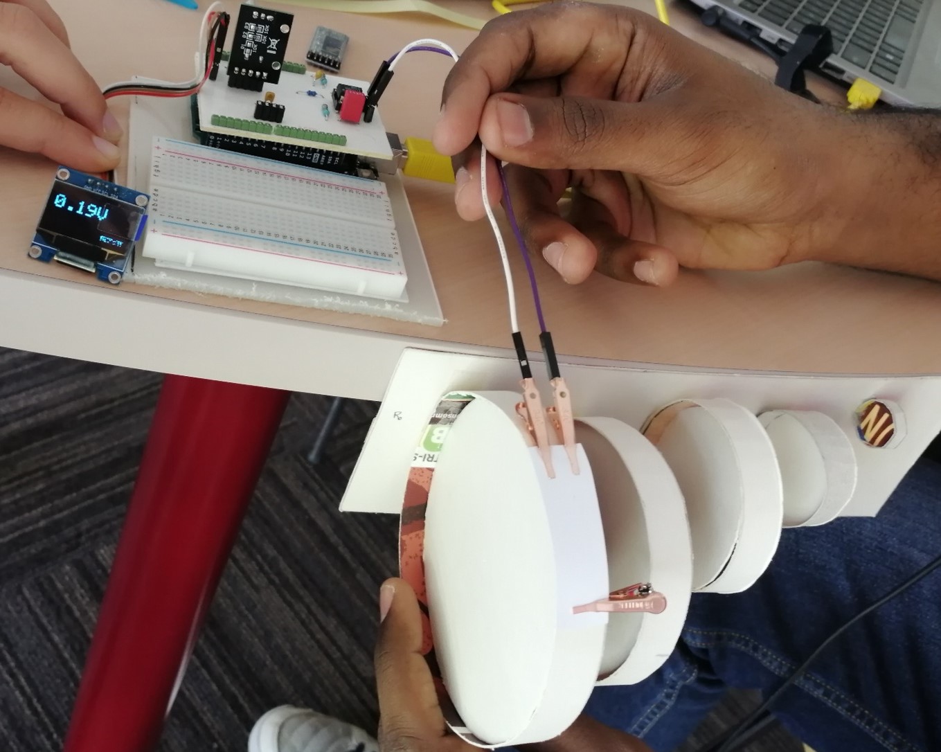
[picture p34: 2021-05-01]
Banc_de_test&résultats/Mesure en compression.jpg

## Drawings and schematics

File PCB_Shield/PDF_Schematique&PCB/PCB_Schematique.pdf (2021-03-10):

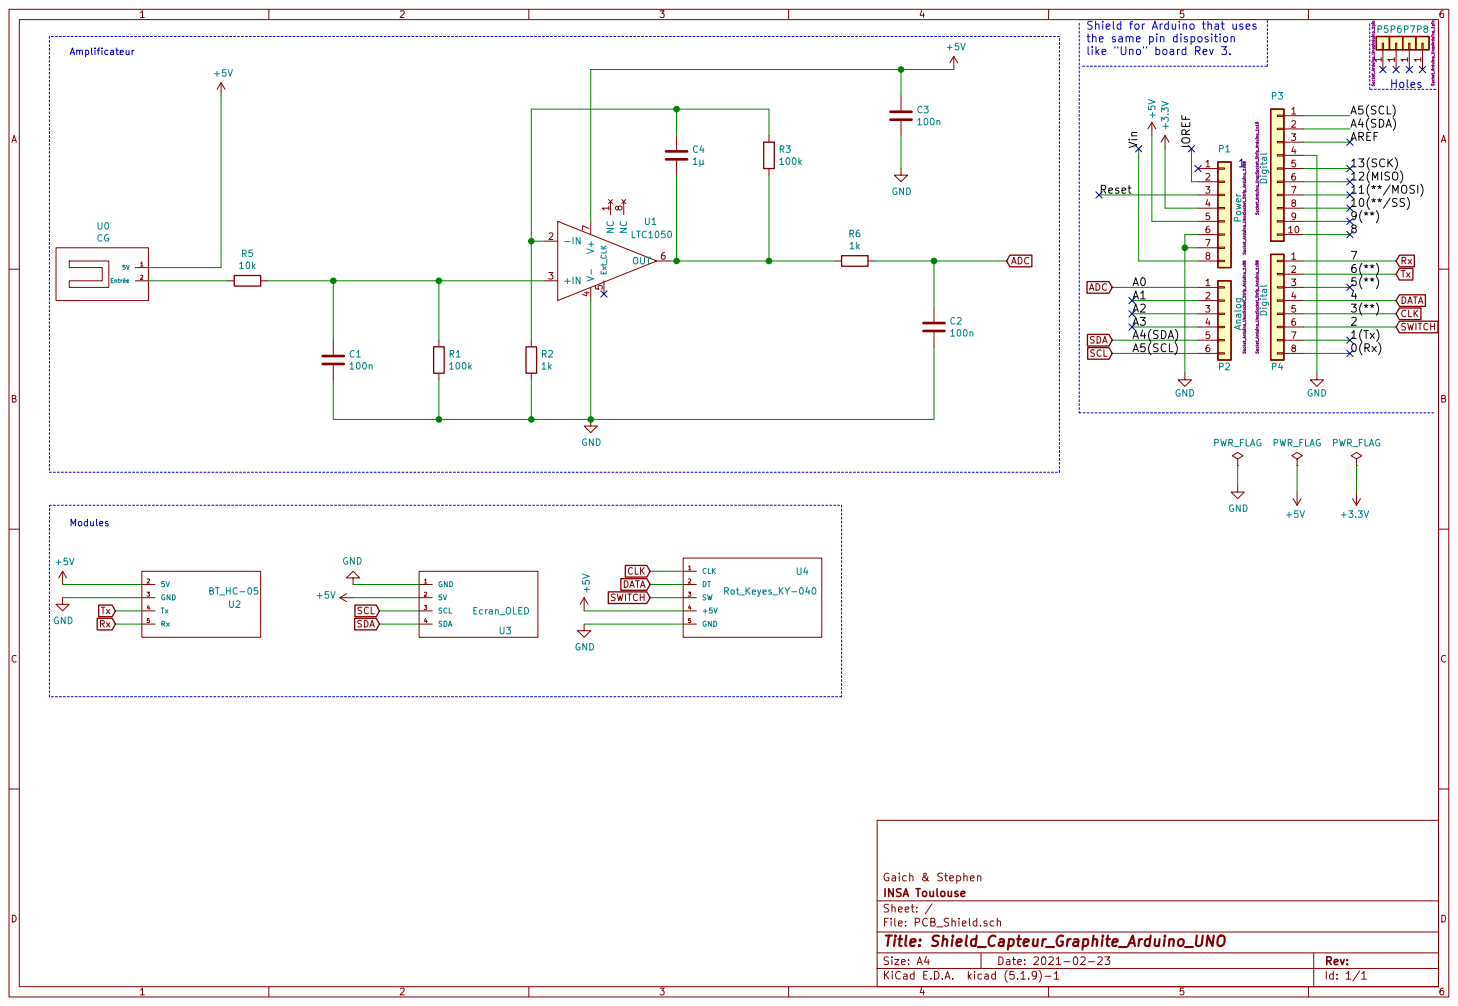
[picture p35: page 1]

the same pin disposition

INSA Toulouse Gaich & Stephen

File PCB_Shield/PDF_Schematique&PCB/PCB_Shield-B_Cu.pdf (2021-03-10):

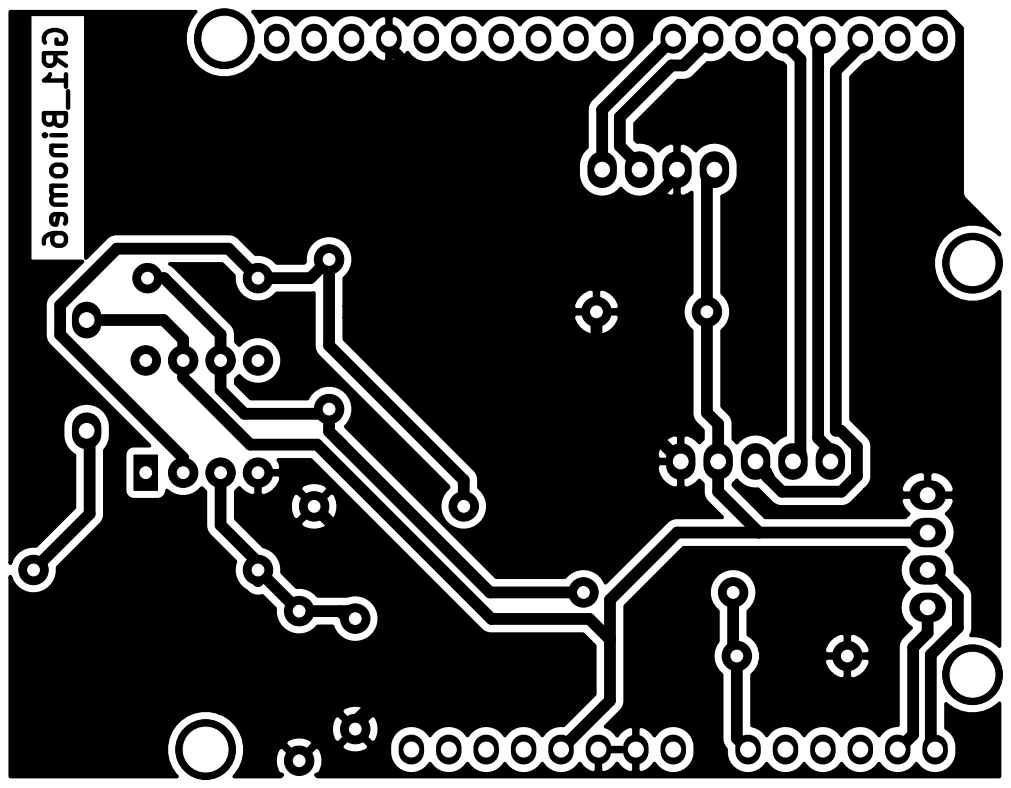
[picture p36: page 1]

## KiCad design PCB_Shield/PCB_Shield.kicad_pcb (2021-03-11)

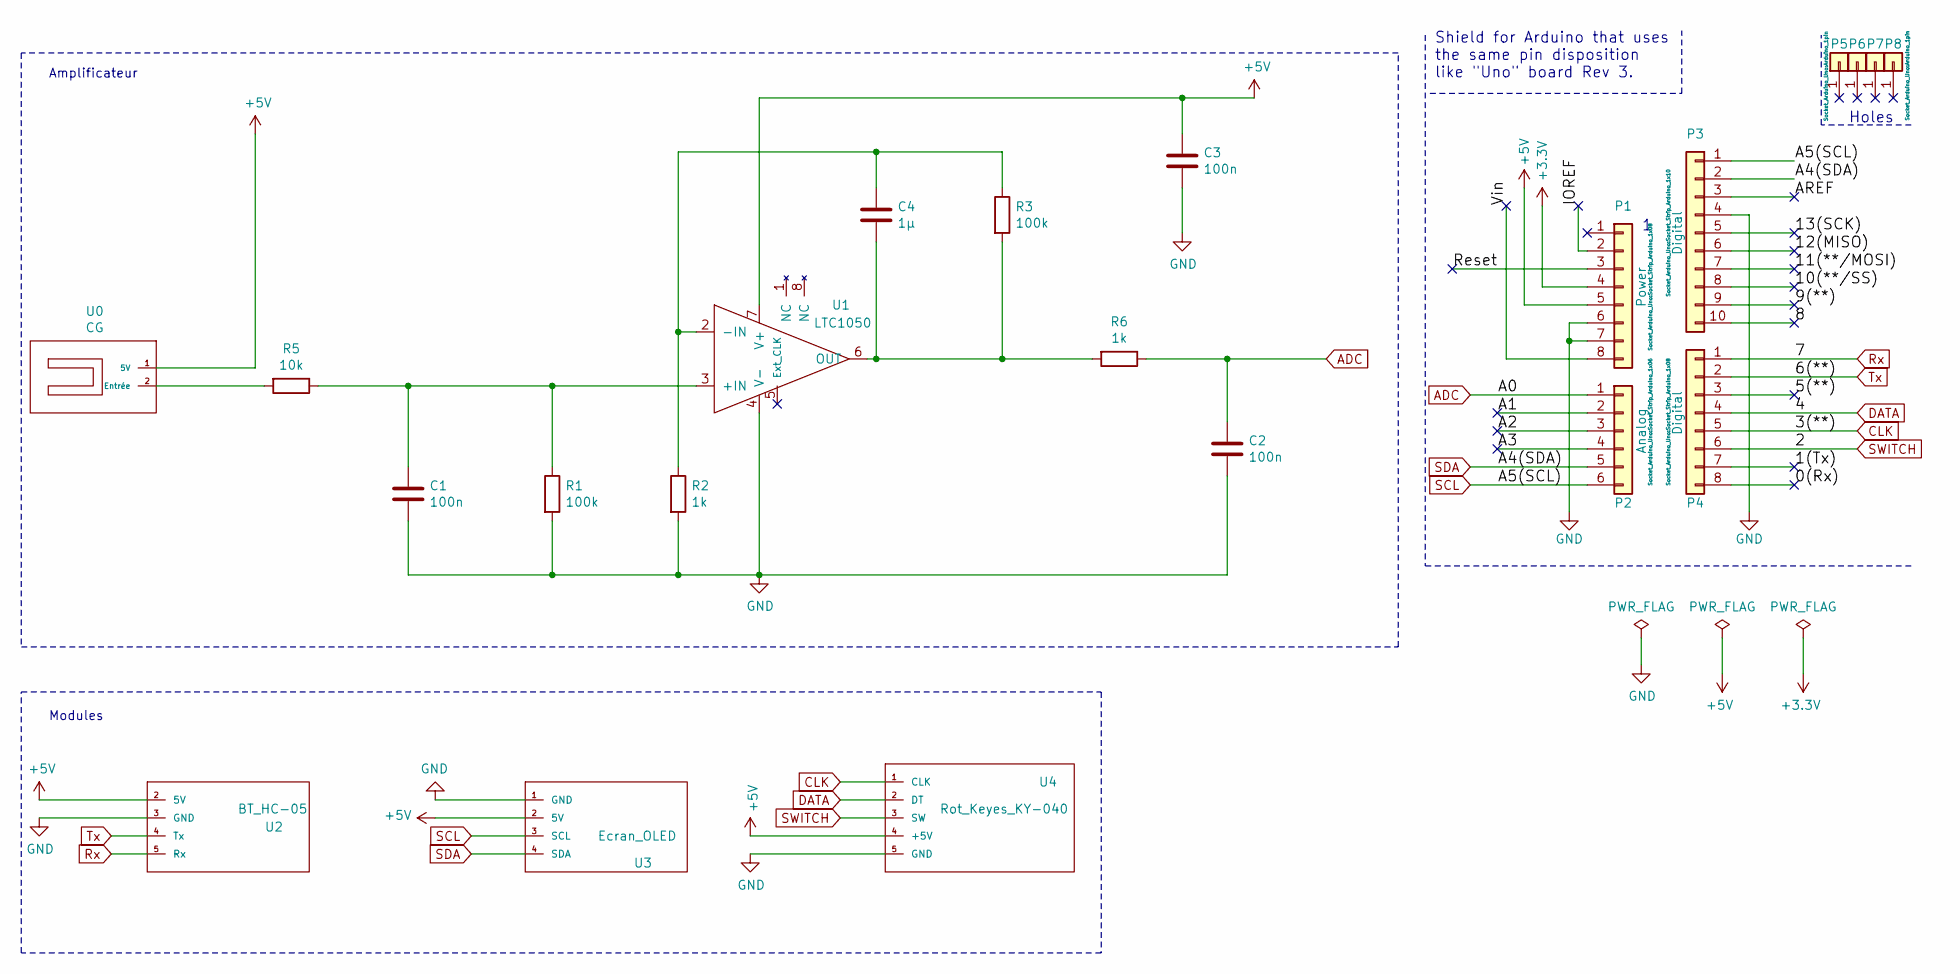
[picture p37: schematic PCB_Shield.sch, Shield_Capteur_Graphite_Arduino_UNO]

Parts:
C1, C2, C3: 100n; C_Axial_L5.1mm_D3.1mm_P7.50mm_Horizontal
C4: 1µ; C_Axial_L5.1mm_D3.1mm_P7.50mm_Horizontal
P1: Power; Socket_Strip_Arduino_1x08
P2: Analog; Socket_Strip_Arduino_1x06
P3: Digital; Socket_Strip_Arduino_1x10
P4: Digital; Socket_Strip_Arduino_1x08
P5, P6, P7, P8: CONN_01X01; Arduino_1pin
R1, R3: 100k; R_Axial_DIN0207_L6.3mm_D2.5mm_P10.16mm_Horizontal
R2, R6: 1k; R_Axial_DIN0207_L6.3mm_D2.5mm_P10.16mm_Horizontal
R5: 10k; R_Axial_DIN0309_L9.0mm_D3.2mm_P15.24mm_Horizontal
U0: CG
U1: LTC1050; DIP-8_W7.62mm_LongPads
U2: BT_HC-05; Bluetooth_HC-05
U3: Ecran_OLED
U4: Rot_Keyes_KY-040; Rot_Keyes_ky-040

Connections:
+3V3: P1.4
+5V: C3.1, P1.5, U0.1 (5V), U1.7 (V+), U2.2 (5V), U3.2 (5V), U4.4 (+5V)
/0(Rx): P4.8
/1(Tx): P4.7
/5(**): P4.3
/8: P3.10
/9(**): P3.9
/10(**/SS): P3.8
/11(**/MOSI): P3.7
/12(MISO): P3.6
/13(SCK): P3.5
/A1: P2.2
/A2: P2.3
/A3: P2.4
/AREF: P3.3
/IOREF: P1.2
/Reset: P1.3
/Vin: P1.8
ADC: C2.1, P2.1, R6.1
CLK: P4.5, U4.1 (CLK)
DATA: P4.4, U4.2 (DT)
GND: C1.2, C2.2, C3.2, P1.6, P1.7, P3.4, R1.2, R2.2, U1.4 (V-), U2.3 (GND), U3.1 (GND), U4.5 (GND)
unnamed: C1.1, R1.1, R5.1, U1.3 (+IN)
unnamed: C4.1, R2.1, R3.1, U1.2 (-IN)
unnamed: C4.2, R3.2, R6.2, U1.6 (OUT)
unnamed: R5.2, U0.2 (Entrée)
Rx: P4.1, U2.5 (Rx)
SCL: P2.6, P3.1, U3.3 (SCL)
SDA: P2.5, P3.2, U3.4 (SDA)
SWITCH: P4.6, U4.3 (SW)
Tx: P4.2, U2.4 (Tx)

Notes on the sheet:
Holes
Shield for Arduino that uses the same pin disposition like "Uno" board Rev 3.
Amplificateur
Modules

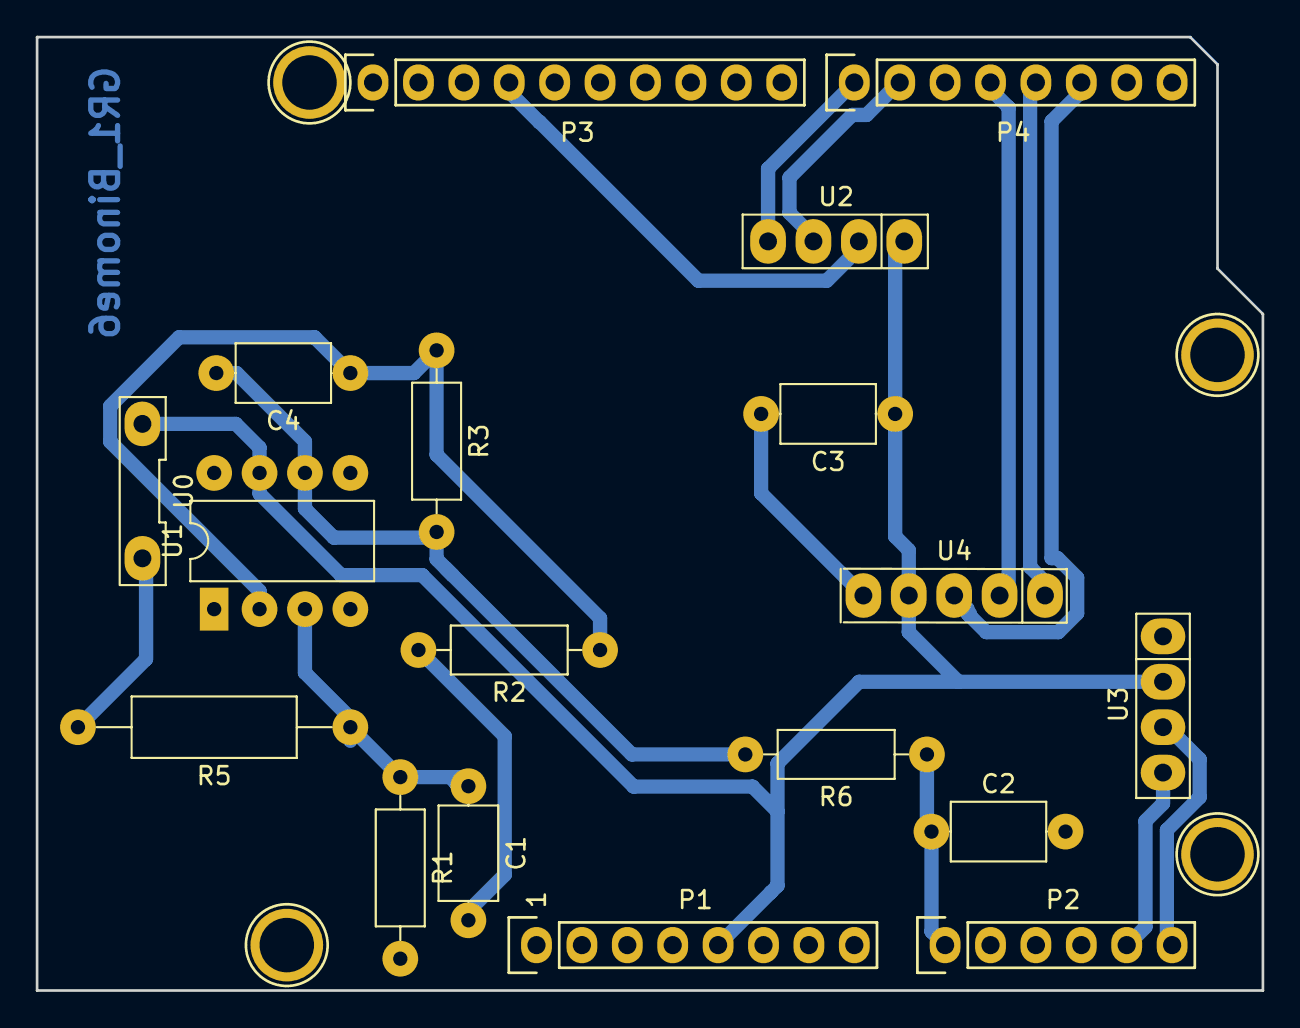
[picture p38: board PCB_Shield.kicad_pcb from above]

Board: 2 copper layers, 68.6 x 53.3 mm, 22 parts (0 on the bottom side), 14 nets.

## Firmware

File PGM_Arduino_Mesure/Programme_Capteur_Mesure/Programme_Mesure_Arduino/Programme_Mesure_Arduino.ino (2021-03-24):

// Variables pour éviter le delay 
unsigned long previousMillis = 0;        // will store last time LED was updated

// constants won't change:
const long interval = 1000;           // interval at which to blink (milliseconds)



//Bluetooth
#include <SoftwareSerial.h>
#define rxPin 6 // Correspondant à la broche tx du module bluetooth
#define txPin 7 // Correspondant à la broche Rx du module bluetooth
#define baudrate 9600 
SoftwareSerial mySerial(rxPin ,txPin); //Definition du software serial

/*//Encodeur rotatoire
#define encoder0PinA  2  //CLK Output A Do not use other pin for clock as we are using interrupt
#define encoder0PinB  4  //DT Output B
#define Switch 5 // Switch connection if available

//OLED
#include <Wire.h>
#include <string.h>
//#undef int
#include <stdio.h>
#include <Adafruit_GFX.h>
#include <Adafruit_GrayOLED.h>
#include <Adafruit_SPITFT.h>
#include <Adafruit_SPITFT_Macros.h>
#include <gfxfont.h>
#include <Adafruit_SSD1306.h>
#include <splash.h>

int OLEDPinSCL = 4;
int OLEDPinSDA = 5;
*/

int capteurgraphitePin = 0;

void setup() {
  // put your setup code here, to run once:
 /* pinMode(OLEDPinSCL, OUTPUT);
  pinMode(OLEDPinSDA, OUTPUT);*/
  pinMode(rxPin,INPUT);
  pinMode(txPin,OUTPUT); 
  mySerial.begin(baudrate);
  Serial.begin(baudrate);

  //encodeur rotatoire
 /* pinMode(encoder0PinA, INPUT); 
  digitalWrite(encoder0PinA, HIGH);       // turn on pullup resistor

  pinMode(encoder0PinB, INPUT); 
  digitalWrite(encoder0PinB, HIGH);       // turn on pullup resistor

  attachInterrupt(0, doEncoder, RISING); // encoder pin on interrupt 0 - pin2 .........doEncoder quand il se passe qqch sur le pin 2

  Serial.begin (9600);
  Serial.println("start");          */      // a personal quirk
  
}

/*void doEncoder() {
  if (digitalRead(encoder0PinB)==HIGH) {
    encoder0Pos++;
  } else {
    encoder0Pos--;
  }
}
*/

/*float getVoltage(int pin){
  
  return (analogRead(pin)*(5/1024.0)); //converting from a 0 to 1023 digital range
                                        // to 0 to 5 volts (each 1 reading equals ~ 5 millivolts
}*/


  
void loop() {
  unsigned long currentMillis = millis ();
  
   if (currentMillis - previousMillis >= interval) {
    // save the last time you blinked the LED
    previousMillis = currentMillis;
    float voltage = analogRead(capteurgraphitePin);
    byte Vadc = map(analogRead(capteurgraphitePin),0,1024,0,255);
    /*String reading = String(voltage, 5);*/
    Serial.write(Vadc);
    mySerial.write(Vadc);
  }
  /*delay(250);*/
  /*Serial.print("Position:");
  Serial.println (encoder0Pos, DEC);  //Angle = (360 / Encoder_Resolution) * encoder0Pos*/
}

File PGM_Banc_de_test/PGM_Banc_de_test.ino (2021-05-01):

#include <SPI.h>
#include <Wire.h>
#include <Adafruit_GFX.h>
#include <Adafruit_SSD1306.h>
#include "Encoder_Polling_V2.h"

// Variables pour éviter le delay 
unsigned long previousMillis = 0;        // will store last time LED was updated

// Variable pour cadencer l'acquisition:
const long interval = 1000;           // interval at which to blink (milliseconds)

// Pin pour mesure de la tension du capteur
int capteurgraphitePin = 0;


// Bluetooth
#include <SoftwareSerial.h>
#define rxPin 6 // Correspondant à la broche tx du module bluetooth
#define txPin 7 // Correspondant à la broche Rx du module bluetooth
#define baudrate 9600 
SoftwareSerial mySerial(rxPin ,txPin); //Definition du software serial

// Variables pour le module encodeur rotatoire 
const int pin_A = 3;  // Encoder input pins
const int pin_B = 4;
int compteur=0;
long lastdebouncetime=0;
long debouncedelay=100;
#define ENC_SW_PIN         2
byte enc_clk, enc_clk_old;
byte enc_switch, enc_switch_old;
String banc;


// Variables pour l'OLED
#define SCREEN_WIDTH 128 // OLED display width, in pixels
#define SCREEN_HEIGHT 64 // OLED display height, in pixels
#define OLED_RESET 4
Adafruit_SSD1306 display(SCREEN_WIDTH, SCREEN_HEIGHT, &Wire, -1);



void setup() {
  Serial.begin(9600); // Initialiser le port série
  encoder_begin();  // Initialiser l'encodeur rotatoire
  attach_encoder(0, pin_A, pin_B);  // Attacher l'encodeur aux pins A et B
  mySerial.begin(baudrate); // Initialiser le port bluetooth
  pinMode (ENC_SW_PIN,INPUT_PULLUP); // Attacher l'intérupteur l'encodeur au pin ENC_SW_PIN
  enc_switch_old = digitalRead(ENC_SW_PIN); // Lire l'état initial de l'intérupteur de l'encodeur rotatoire
  display.begin(SSD1306_SWITCHCAPVCC, 0x3C); // Initialiser l'affichage
  display.clearDisplay();
  display.setTextSize(1);
  display.setCursor(0, 10);
  display.display();
 
}



// fonction qui permet de bloquer le program tant que l'intérupteur de l'encodeur n'est pas appuyé
int buttonclicked(){
   while(enc_switch ==1){
    enc_switch=digitalRead(ENC_SW_PIN);
    if((enc_switch_old == 1) && (enc_switch == 0)) {// 1->0 transition
      delay(300);
      enc_switch=enc_switch_old;
      return 1;
    }
   }
}

// fonction qui permet d'afficher toutes les choix du banc de test
// permet également de surligner une des choix en fonction de la position de l'encodeur rotatoire
// stocke dans le string banc le type de banc de test selectionné

void buildmenu(int choix){
  display.clearDisplay();
  display.setTextSize(1);
  display.setCursor(0, 10);
  display.setTextColor(WHITE);
  display.println("Menu Principal");
  if(choix==0){
   display.setTextColor(BLACK,WHITE);
   display.println("Banc de test dechets");
   display.setTextColor(WHITE);
   display.println("Banc de test carton");
   display.println("Banc de teste imprime");
   display.println("Mesure");
   display.display();
   banc="Banc de test dechets";
  }
  if(choix==1){
   display.setTextColor(WHITE);
   display.println("Banc de test dechets");
   display.setTextColor(BLACK,WHITE);
   display.println("Banc de test carton");
   display.setTextColor(WHITE);
   display.println("Banc de teste imprime");
   display.println("Mesure");
   display.display();
   banc="Banc de test carton";
  }
  if(choix==2){
   display.setTextColor(WHITE);
   display.println("Banc de test dechets");
   display.println("Banc de test carton");
    display.setTextColor(BLACK,WHITE);
   display.println("Banc de teste imprime");
   display.setTextColor(WHITE);
   display.println("Mesure");
   display.display();
   banc="Banc de test imprimé";
  }
  if(choix==3){
   display.setTextColor(WHITE);
   display.println("Banc de test dechets");
   display.println("Banc de test carton");
   display.println("Banc de teste imprime");
   display.setTextColor(BLACK,WHITE);
   display.println("Mesure");
   display.display();
   banc="Mesure";
  }
  

  
}

// permet d'afficher les textes une après l'autre pour demander à l'utilisateur si le bluetooth est connecté
// puis si l'utilisateur est pret
void submenu(){
  //1er etape
  display.clearDisplay();
  display.setTextSize(1);
  display.setCursor(0, 10);
  display.setTextColor(WHITE);
  display.println("Le bluetooth est-il connecte?");
  display.setTextColor(BLACK,WHITE);
  display.println("Oui");
  display.display();
  buttonclicked();
  display.clearDisplay();
  display.setTextSize(1);
  display.setCursor(0, 10);
  display.setTextColor(WHITE);
  display.println("Etes vous prets?");
  display.setTextColor(BLACK,WHITE);
  display.println("Oui");
  display.display();
  buttonclicked();
  mesure();
 
}

// fonction qui permet de mesurer la tension sur le pin "capteurgraphite", l'afficher sur l'OLED et l'envoyer sur le port bluetooth

int mesure(){
  while(enc_switch ==1){
    enc_switch=digitalRead(ENC_SW_PIN);
    unsigned long currentMillis = millis ();
   if (currentMillis - previousMillis >= interval) {

    previousMillis = currentMillis;
   float voltage = getVoltage(capteurgraphitePin);
   byte Vadc = map(analogRead(capteurgraphitePin),0,1024,0,255); // permet de coder la mesure sur 1 byte
    display.clearDisplay();
    display.setTextSize(3);
    display.setCursor(0, 10);
    display.setTextColor(WHITE);
    display.print(voltage);
    display.println("V");
    display.setTextSize(1);
    display.setTextColor(BLACK,WHITE);
    display.println("STOP");
    display.display();
    mySerial.write(Vadc);
   }
    if((enc_switch_old == 1) && (enc_switch == 0)) {// 1->0 transition
      delay(300);
      enc_switch=enc_switch_old;
      return 1;
    }
  }
  
}

// fonction qui permet de lire la valeur de la tension sur le pin 'capteurgraphite'
float getVoltage(int pin){
  return (analogRead(pin)*(5/1024.0)); //convertir de 0 à 1023 digital range
                                        // à 0 à 5 volts 
}

// fonction qui permet de lire en permanence la position de l'encodeur rotatoire
// et en utilisant la fonction buildmenu() permet de surligner une des choix de type de banc de test
int mainmenu(){
  int compteurmenu=0;
  buildmenu(0);
 enc_switch=digitalRead(ENC_SW_PIN);
  while(enc_switch ==1){
  enc_switch=digitalRead(ENC_SW_PIN);
  int dir_0 = encoder_data(0);  // First encoder
  if(dir_0!=0){
  if(millis()-lastdebouncetime>debouncedelay){
    lastdebouncetime=millis();
    compteurmenu=compteurmenu+1;
  }
  }
  if(compteurmenu==4){
    compteurmenu=compteurmenu-4;
  }
  buildmenu(compteurmenu);

  if((enc_switch_old == 1) && (enc_switch == 0)) {
    delay(300);
    enc_switch = enc_switch_old; 
    return 1;

    }
  }
}


void loop() {
  mainmenu();
  submenu();

}

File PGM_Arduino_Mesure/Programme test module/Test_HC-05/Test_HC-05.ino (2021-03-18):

#include <SoftwareSerial.h>
#define rxPin 6 //Broche 11 en tant que RX, � raccorder sur TX du HC-05
#define txPin 7 //Broche 10 en tant que RX, � raccorder sur TX du HC-05
#define baudrate 9600
SoftwareSerial mySerial(rxPin ,txPin); //D�finition du software serial

void setup(){
  pinMode(rxPin,INPUT);
  pinMode(txPin,OUTPUT);
    
  mySerial.begin(baudrate);
  Serial.begin(baudrate);
}

void loop(){
    int i = 0; 
	char someChar[32] ={0};
	//when characters arrive over the serial port...

	while (Serial.available()) {
	   do{
		someChar[i++] = Serial.read();
		delay(3);		
	   }while (Serial.available() > 0);
	   
	   mySerial.println(someChar); 
	   Serial.println(someChar); 
	}
	while (mySerial.available()) {
		Serial.print((char)mySerial.read());
	}
}

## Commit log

2021-03-03 Ajout de la partie PCB Shield au projet Capteur_Graphite.
    [PCB_Shield.kicad_pcb, PCB_Shield.sch]
2021-03-08 Modification PCB _ test routage
    [PCB_Shield.kicad_pcb]
2021-03-11 Modif 11-03
    [PCB_Shield.kicad_pcb]
2021-03-18 Modif 18-03
    [PCB_Shield_rectification_OLED.kicad_pcb]
2021-04-10 Banc de test news
    [Plan d'expérience.xlsx]
2021-04-12 Modif 12-4
    [Plan d'expérience.xlsx]
2021-04-13 Modif 13-04
    [Plan d'expérience.xlsx]
2021-04-13 Modelisation capteur
    [Modelisation_capteur.dxf]
2021-04-13 Modif 13-4 21h20
    [Mesure_RayonCoubure_Crayons_Papiers.xlsx, Plan d'expérience.xlsx, Plan d'expérience_meilleures_dimensions.xlsx]
2021-04-16 Banc de test mise à jour
2021-04-16 Modif matrice hadamard
    [Plan d'expérience_meilleures_dimensions.xlsx]
2021-04-19 Banc de test
    [Modelisation_capteur.dxf, Plan d'expérience_meilleures_dimensions.xlsx]
2021-04-21 Banc de test_DOE
    [Plan d'expérience_meilleures_dimensions.xlsx]
2021-04-21 A faire readme
    [#Capteurs_plan_experience.dxf, Capteurs_plan_experience.dxf]
2021-04-22 Banc de test session 22-04
    [Mesure_RayonCoubure_Crayons_Papiers.xlsx]
2021-04-26 Modif Banc de test
2021-04-26 Modifier 26-04
    [Mesure_RayonCoubure_Crayons_Papiers.xlsx, Modelisation_capteur.dxf]
2021-04-27 Commentaires Mesures
    [Plan d'expérience_meilleures_dimensions.xlsx]
2021-04-28 Modif Courbes
    [Mesure_RayonCoubure_Crayons_Papiers.xlsx]
2021-05-01 Completer datasheet
    [Mesure_RayonCoubure_Crayons_Papiers.xlsx]
2021-05-01 Modif graphes zone de non destruction et mis à jour du code banc de test
    [Determination_zone_non_destruction_capteur.xlsx, Mesure_RayonCoubure_Crayons_Papiers.xlsx]
2021-05-01 Modif program banc de test
2021-05-01 Mis en forme et commentaire pour le code banc de test et PGM Captuer Mesure
2021-05-02 Figures determination zone de non destruction
2021-05-03 Excel Determination_zone_non_destruction_capteur
    [Determination_zone_non_destruction_capteur.xlsx]
2021-05-05 Suppression pour avoir commentaire "commit" de FIN DE PROJET
    [#Capteurs_plan_experience.dxf, Capteurs_plan_experience.dxf, Determination_zone_non_destruction_capteur.xlsx, Encoder KY-040.SLDPRT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]
2021-05-05 FIN DE PROJET
    [#Capteurs_plan_experience.dxf, Capteurs_plan_experience.dxf, Determination_zone_non_destruction_capteur.xlsx, Encoder KY-040.SLDPRT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]
